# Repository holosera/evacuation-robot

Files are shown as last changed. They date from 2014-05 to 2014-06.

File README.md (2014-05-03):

evacuation-robot
================

Robot for automated evacuation of exetainer vials used in research.

Frame (acrylic sheets)

3d Printed mechanical parts 

Custom electronics (pcb and schematics)

Additional parts list

Filetypes:
.scad -> Openscad

.svg -> Inkscape

.ino -> Arduino IDE

.dxf -> Inkscape

.stl -> Meshlab

.brd -> Eagle

.sch -> Eagle

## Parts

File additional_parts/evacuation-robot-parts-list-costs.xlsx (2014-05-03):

Mechanical parts | Part # | suppliers | amount | costs $US |  | suppliers
Linear actuator Firgelli | L12-30-100-6-R | a,f | 1 | 100 |  | a | robotshop.com / robotshop.ca
Nema 17 stepper low voltage | 2.8 V 1.68A 4.4 kg-cm RepRap Stepper Motor | a,b | 1 | 30 |  | b | pololu.com
timing belt 140XL | 140XL 3/16 wide (can cut wider one) | d,e | 1 | 10 |  | c | mouser.com
hardened precsion ground shaft 8x50mm | 6112K44 | d | 2 | 10 |  | d | mcmastercarr
linear ball bearing LM8UU | LM8UU | e | 2 | 10 |  | e | ebay
Solenoid valves | U8256B045V 24volt DC (12v also works) | h | 3 | 150 |  | f | firgelli.com
Brass tee 1/8 NPT Female × Male × Female Tees | 50785K325 | d | 2 | 10 |  | g | http://www.posifamicrosystems.com/
Brass tee 1/8 NPT Female × Female × Male Tees | 50785K225 | d | 1 | 5 |  | h | valveshop.com
Medium Pressure Brass Hex Nipple 1/8 NPT | 5485K21 | d | 3 | 5
Straight Adapter for 1/4" Tube OD x 1/8 NPT Male | 5272K299 | d | 3 | 15 |  | u | none, build yourself
Straight Connector for 1/4" Tube OD | 5272K221 | d | 1 | 5
1/4 od x 1/8 id ptfe/pva tubing (1ft) |  |  | 1 | 5
1/4 od stainless steel tubing (1ft) |  |  | 1 | 5
Easy-to-Form 260 Brass | 7782T111 | d | 1 | 6
Luer lock to tube adapter | 51465K115 | d | 1 | 7
688zz ball bearing | 688zz | d | 2 | 10
Frame parts | Part # | suppliers | amount | costs $US
1/4 Acrylic sheet preferably cast | 8560K435 | d | 1 | 100
3d printed parts | minumum of 6 but up to 12 printed parts | u | x | 250 | (5 hours print time on reprap)
fasteners | #6 woodscrews, some M3 bolts | d |  | 10
Electronics | Part # | suppliers | amount | costs $US
Arduino Uno or compatible | Arduino Uno R3 | a,b,c,e | 1 | 25
Stepper motor driver DRV8825 | DRV8825 | a,b,f | 1 | 15
I2C LCD module 16x2 or 4x20 | RB-Dfr-69 or RB-Dfr-146 | a,b,c, | 1 | 25
vacuum sensor PVC1003 | PVC1003 | g | 0 | 0
EPCOS 5K thermistor for vacuum | 871-B57540G502F | c | 2 | 10 | 1 spare
PCB 1 (arduino shield) |  | u | 1 | 40
PCB 2 (vacuum sensor controller) |  | u | 1 | 30
PCB 3 (endstop) |  | u | 1 | 15
PCB 4 (rotary encoder) |  | u | 1 | 20
hookup wire, crimp connectors |  | b,c |  | 10
Power supply 12V DC 3A UL/CSA |  | a,b,c | 1 | 15
 |  | estimated | TOTAL | 948 | US dollar

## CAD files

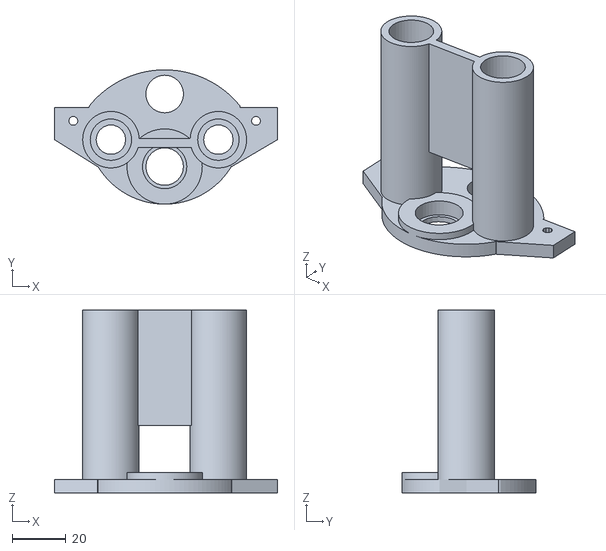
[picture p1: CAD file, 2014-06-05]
3d-printed-parts/Front-plate.stl
83.0 x 50.0 x 68.0

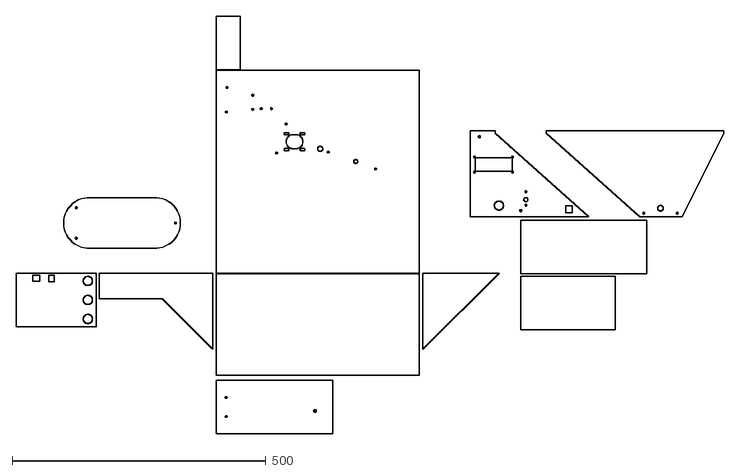
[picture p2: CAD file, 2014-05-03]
frame-sheets/acrylic_6mm_sheets.dxf
1393.8 x 822.0

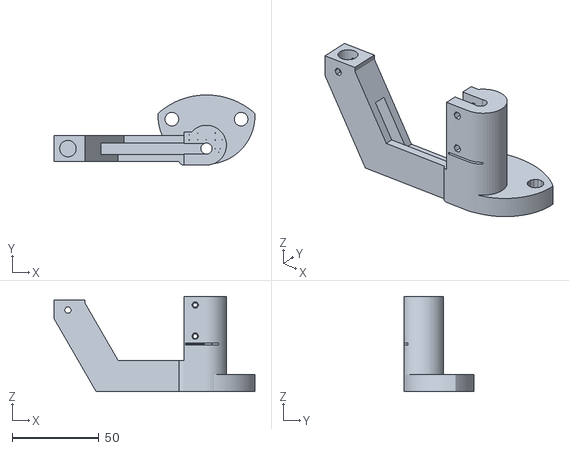
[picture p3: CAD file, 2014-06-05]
3d-printed-parts/Sled.stl
116.0 x 40.5 x 55.0

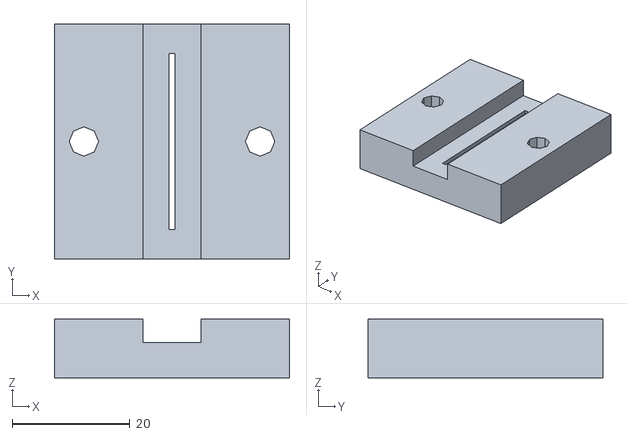
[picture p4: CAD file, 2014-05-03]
3d-printed-parts/belt-splitter_3-8_to_5mm.stl
40.0 x 40.0 x 10.0

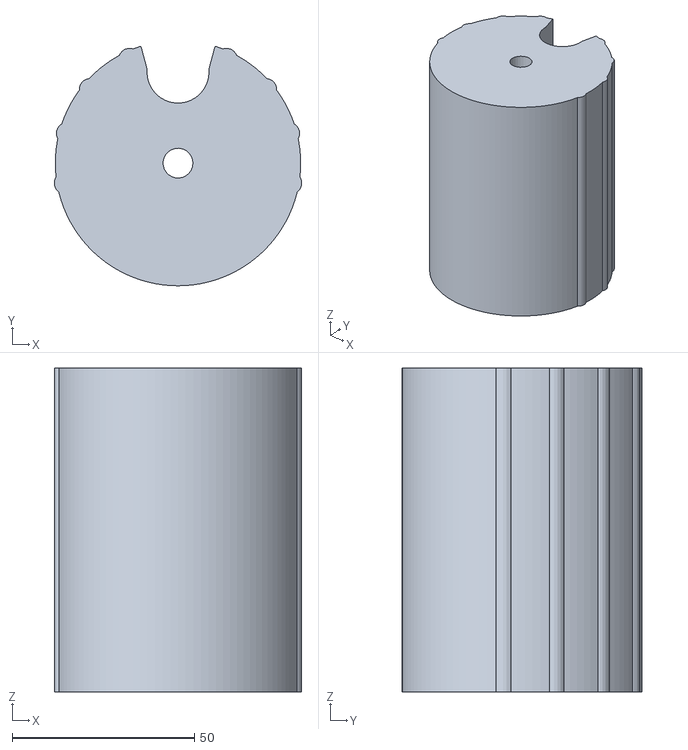
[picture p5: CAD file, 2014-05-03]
3d-printed-parts/Rotor.stl
68.0 x 65.8 x 89.0

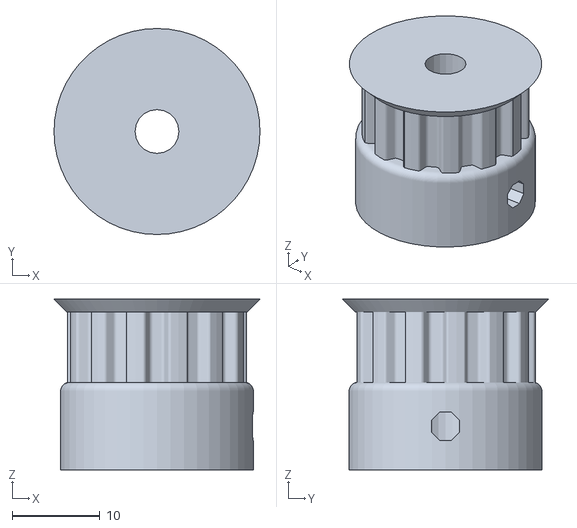
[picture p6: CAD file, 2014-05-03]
3d-printed-parts/Pulley_13T-XL.stl
23.5 x 23.5 x 19.5

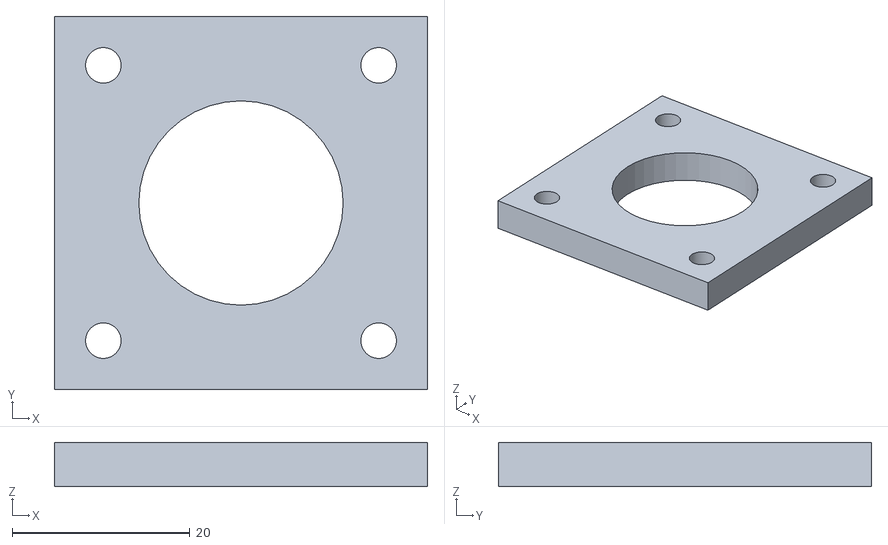
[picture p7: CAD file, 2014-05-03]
3d-printed-parts/Stepper_spacer.stl
42.0 x 42.0 x 5.00

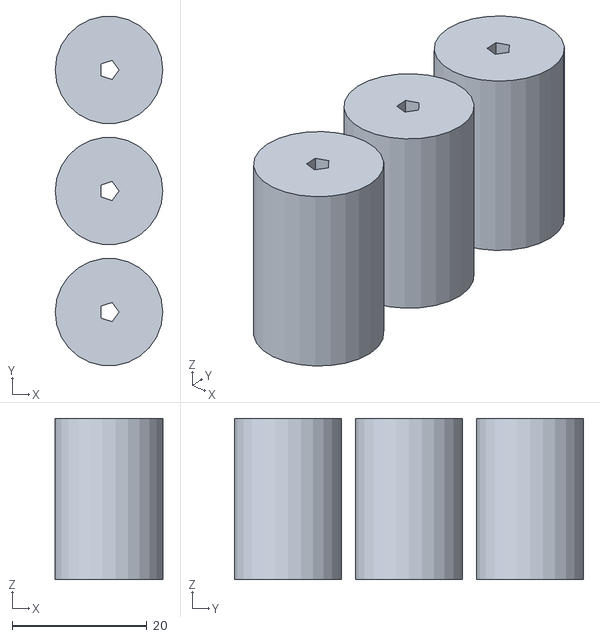
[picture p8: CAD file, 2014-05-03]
3d-printed-parts/Belt-protector-spacers.stl
16.0 x 51.9 x 24.0

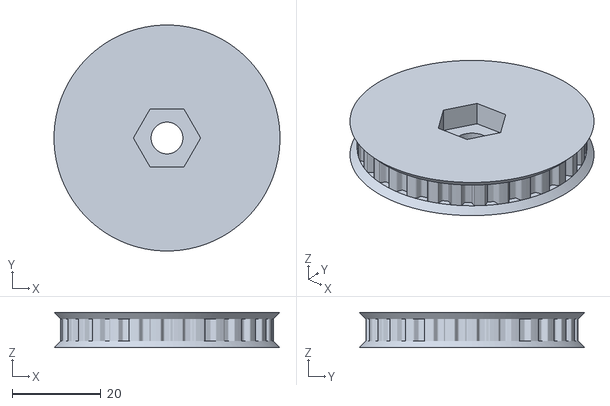
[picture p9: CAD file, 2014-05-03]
3d-printed-parts/Pulley_30T-XL.stl
51.0 x 51.0 x 8.00

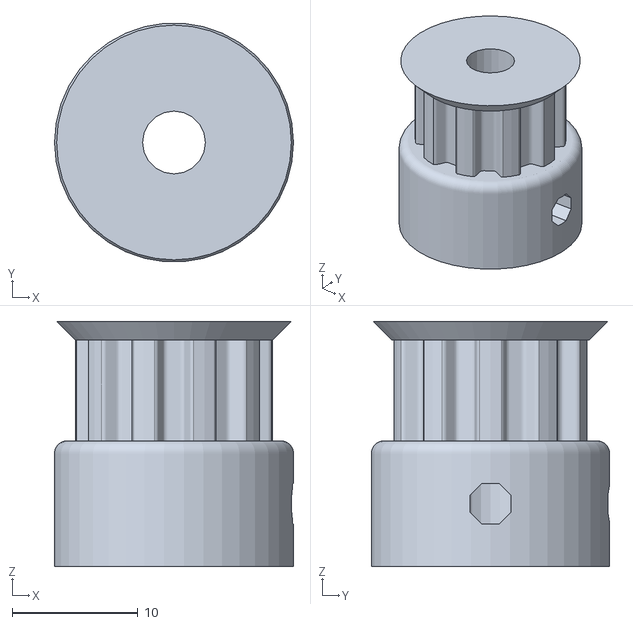
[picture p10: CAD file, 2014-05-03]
3d-printed-parts/Pulley_10T-XL.stl
19.0 x 18.9 x 19.5

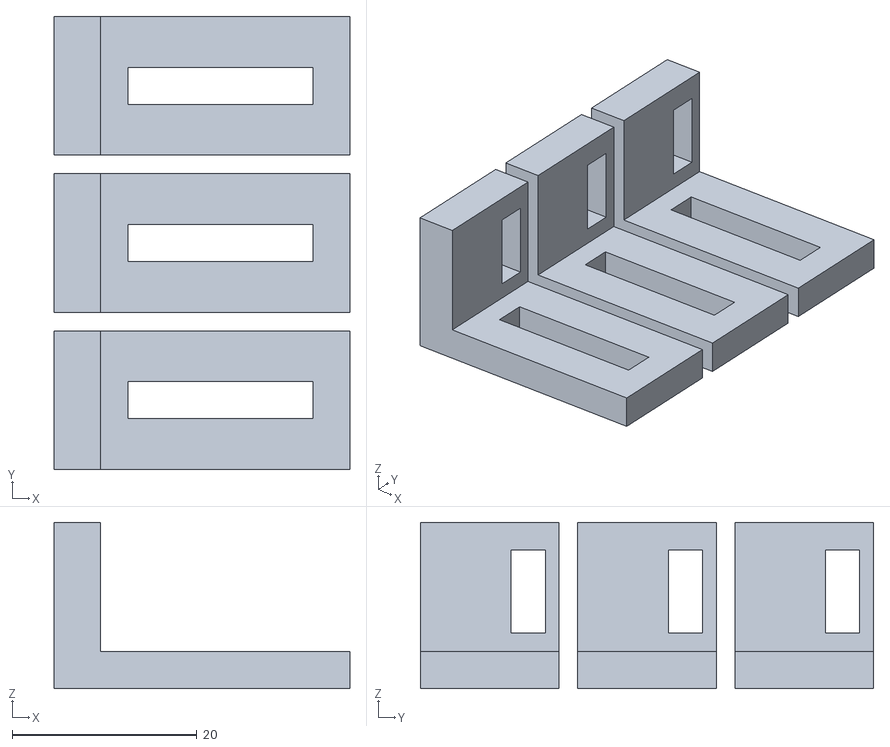
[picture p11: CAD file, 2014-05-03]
3d-printed-parts/Opto-endstop-pcb_mount.stl
32.0 x 49.0 x 18.0

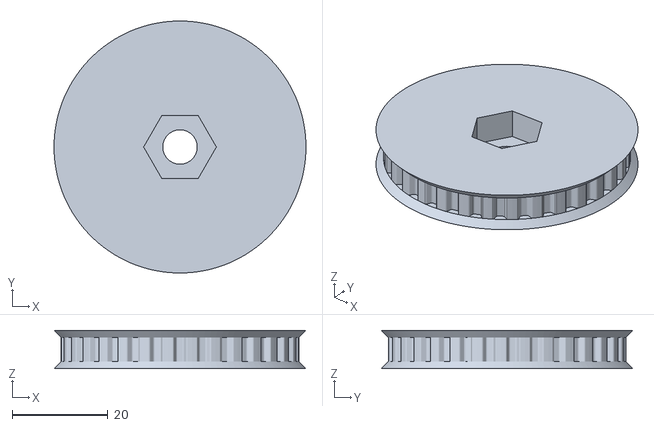
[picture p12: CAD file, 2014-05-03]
3d-printed-parts/Pulley_31T-XL.stl
52.6 x 52.6 x 8.00

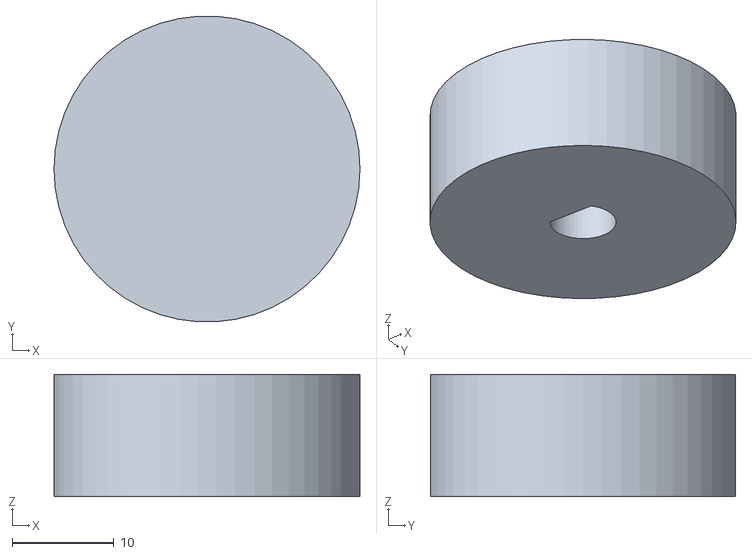
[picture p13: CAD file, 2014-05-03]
3d-printed-parts/Rotary-encoder-knob.stl
30.0 x 29.9 x 12.0

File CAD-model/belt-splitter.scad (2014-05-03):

difference(){
	translate([-20,0,0])
	cube([40,40,10]);
	translate([-4.9,-1,6])
	cube([9.8,50,50]);
	translate([-0.5,5,-1])
	cube([1,30,50]);


	translate([-15,20,-1])
	cylinder(r=2.5,h=100);
	translate([15,20,-1])
	cylinder(r=2.5,h=100);
}

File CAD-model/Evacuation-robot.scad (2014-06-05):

display=0;

sheet_thickness=6.25;
backplate_width=400;
backplate_height=400;
bottomplate_depth=200;

sideplate_height=150;
sideplate_depth=150;

slide_width=105;

//---------------------------------------------------------------------------
//_____________________ACRYLIC SHEETS__________________________________________

module bottomplate (){
	difference(){
		union(){
			translate([0,-bottomplate_depth,0])
			cube([backplate_width,bottomplate_depth,sheet_thickness]);
		}
	}
}

module backplate (){
	difference(){
		union(){
			translate([0,0,0])
			cube([backplate_width,sheet_thickness,backplate_height]);
		}
		translate([275,20,220])
		rotate([90,0,0])
		cylinder(r=4,h=100);		
	}
}

module beltplate (){
	union(){
		difference(){
			union(){
				translate([50,50,0])
				cylinder(r=50,h=sheet_thickness);	
				translate([180,50,0])
				cylinder(r=50,h=sheet_thickness);	
			}	
		translate([50,0,-1])
		cube([130,100,sheet_thickness+2]);
		}
		translate([50,0,0])
		cube([130,100,sheet_thickness]);	
	}	
}

module beltplate_holes (){
	translate([25,80,-50])
	cylinder(r=1.7,h=100);
	translate([25,20,-50])
	cylinder(r=1.7,h=100);

	translate([230-10,50,-50])
	cylinder(r=1.7,h=100);
}


module sideplateleft(){
	union(){
		translate([sheet_thickness,0,sheet_thickness])
		rotate([0,-90,0])
		linear_extrude(height=sheet_thickness)
		polygon(points=[[0,0],[0,-sideplate_depth],[sideplate_height,0]], paths=[[0,1,2]]);
		
		translate([0,-50,sheet_thickness])
		cube([sheet_thickness,50,230-sheet_thickness]);
	}
}

module sideplateright(){

	translate([backplate_width,0,sheet_thickness])
	rotate([0,-90,0])
	linear_extrude(height=sheet_thickness)

	polygon(points=[[0,0],[0,-sideplate_depth],[sideplate_height,0]], paths=[[0,1,2]]);

}

module leftslide(){
	cube([248,slide_width,sheet_thickness]);
}

module rightslide(){
	cube([186,slide_width,sheet_thickness]);
}

module slidefront(){
	difference(){
		linear_extrude(height=	sheet_thickness)
		polygon(points=[[50,0],[50,5],[234,170],[318,170],[backplate_width,5],[backplate_width,0]] , paths=[[0,1,2,3,4,5]]);	
	
	}
}

module elecfront(){
	difference(){
		translate([0,-sheet_thickness-slide_width,backplate_height])
		rotate([-90,0,0])
		linear_extrude(height=
	sheet_thickness)
		polygon(points=[[0,0],[0,170],[234,170],[50,5],[50,0]] , paths=[[0,1,2,3,4,5]]);	
	
	}
}

module elecleft (){
	difference(){
		translate([0,-slide_width,230+sheet_thickness])
		cube([sheet_thickness,slide_width,	backplate_height-230-sheet_thickness*2]);
	}
}

module electop (){
	difference(){
		translate([0,-slide_width,backplate_height-sheet_thickness])
		cube([48,slide_width,sheet_thickness]);
	}
}

module elecbottom (){
	difference(){
		translate([0,-slide_width,230])
		cube([234-4,slide_width,sheet_thickness]);
	}
}

module elecfront_connectors (){
	difference(){
		cube([24,sheet_thickness,12]);
		translate([12,-1,6])
		rotate([-90,0,0])
		cylinder(r=1.7,h=100);
	}


}

//-------------------------------------------------------------------------
//___________________________3D PRINTED PARTS______________________________

module rotor(){
	difference(){
		union(){
			translate([0,0,0])
			cylinder(r=33.7,h=89,$fn=100);
			for ( i = [-100,-75,-50,-25,0,25,50,75,100] )
			{
			    rotate( [0, 0,  i ])
			    translate([0, 31.5, 0])
			    cylinder(r=3,h=89,$fn=20);
			}
		}	
		translate([0,25,-1])
		cylinder(r=8.6,h=110,$fn=50);
		translate([0,27,-1])
		cylinder(r=8.7,h=110,$fn=50);

		translate([-8,24,-1]) 
		rotate([0,0,15])
		cube([5,40,110]);

		translate([8,24,-1])
		rotate([0,0,-15])
		translate([-5,0,0])
		cube([5,40,110]);

		translate([0,0,-2])
		cylinder(r=4.1,h=150,$fn=25);
	}
}

module sled(){
	difference(){
		union(){
			intersection(){
				translate([0,-8,0])	
				cylinder(r=28,h=10,$fn=100);
				translate([0,-38,-1])	
				cylinder(r=42,h=15,$fn=100);	
			}		

			translate([-13,-33.5,0])	
			cylinder(r=3,h=18,$fn=50);

			translate([0,-25,0])	
			cylinder(r=11.5,h=55,$fn=50);

			translate([-13,-36.5,0])
			cube([13,19,55]);

			translate([-63.7,-34.5,0])
			cube([64,15,12]);

			translate([-63.7,-34.5,0])
			cube([64,7,18]);

			translate([-88,-34.5,42])
			cube([18,15,11]);
			translate([-63.7,-34.5,0])
			rotate([0,-30,0])
			cube([20,15,48.66]);
		}	
	translate([0,-27,-1])	
	cylinder(r=3.25,h=100,$fn=20);
	translate([20,-10,-1])	
	cylinder(r=4,h=50);
	translate([-20,-10,-1])	
	cylinder(r=4,h=50);

	translate([-50,-30.25,3])	
	cube([50,6.50,24.5]);		
	translate([-50,-30,27])	
	cube([50,6,50]);	

	translate([-12,-50.0,27])	
	cube([19,22,1]);	


	translate([-6.5,0,32])	
	rotate([90,0,0])
	cylinder(r=1.4,h=100,$fn=6);	
	translate([-6.5,0,50])	
	rotate([90,0,0])
	cylinder(r=1.4,h=100,$fn=6);	

	translate([-6.5,-25,32])	
	rotate([90,0,0])
	cylinder(r=2,h=100,$fn=6);	
	translate([-6.5,-25,50])	
	rotate([90,0,0])
	cylinder(r=2,h=100,$fn=6);	

	translate([-100,-30.3,3])
	cube([54,6.5,32]);

	translate([-80,-27,15.5+28])	
	cylinder(r=4.8,h=100,$fn=20);

	translate([-80,-40,19+28])	
	rotate([-90,0,0])
	cylinder(r=2,h=100,$fn=6);


	//reinforcement
	translate([0,-22,-1])	
	cylinder(r=0.2,h=100);

	translate([-5,-22,-1])	
	cylinder(r=0.2,h=100);
	translate([5,-22,-1])	
	cylinder(r=0.2,h=100);
	translate([9,-22,-1])	
	cylinder(r=0.2,h=100);

	translate([-10,-19,-1])	
	cylinder(r=0.2,h=100);
	translate([-10,-22,-1])	
	cylinder(r=0.2,h=100);
	translate([-5,-18,-1])	
	cylinder(r=0.2,h=100);
	translate([0,-18,-1])	
	cylinder(r=0.2,h=100);
	translate([5,-18,-1])	
	cylinder(r=0.2,h=100);

	translate([5,-27,-1])	
	cylinder(r=0.2,h=100);
	translate([8,-27,-1])	
	cylinder(r=0.2,h=100);
	translate([7,-29,-1])	
	cylinder(r=0.2,h=100);
	}
	
}

module sled_old(){
	difference(){
		union(){
			intersection(){
				translate([0,-8,0])	
				cylinder(r=28,h=10,$fn=100);
				translate([0,-38,-1])	
				cylinder(r=42,h=15,$fn=100);	
			}		

			translate([-13,-33.5,0])	
			cylinder(r=3,h=18,$fn=50);

			translate([0,-25,0])	
			cylinder(r=11.5,h=55,$fn=50);

			translate([-13,-36.5,0])
			cube([13,19,55]);

			translate([-60.7,-34.5,0])
			cube([61,15,12]);

			translate([-60.7,-34.5,0])
			cube([61,7,18]);

			translate([-85,-34.5,42])
			cube([18,15,11]);
			translate([-60.7,-34.5,0])
			rotate([0,-30,0])
			cube([20,15,48.66]);
		}	
	translate([0,-27,-1])	
	cylinder(r=3.25,h=100,$fn=20);
	translate([20,-10,-1])	
	cylinder(r=4,h=50);
	translate([-20,-10,-1])	
	cylinder(r=4,h=50);

	translate([-50,-30.25,3])	
	cube([50,6.50,24.5]);		
	translate([-50,-30,27])	
	cube([50,6,50]);	

	translate([-12,-50.0,27])	
	cube([19,22,1]);	


	translate([-6.5,0,32])	
	rotate([90,0,0])
	cylinder(r=1.4,h=100,$fn=6);	
	translate([-6.5,0,50])	
	rotate([90,0,0])
	cylinder(r=1.4,h=100,$fn=6);	

	translate([-6.5,-25,32])	
	rotate([90,0,0])
	cylinder(r=2,h=100,$fn=6);	
	translate([-6.5,-25,50])	
	rotate([90,0,0])
	cylinder(r=2,h=100,$fn=6);	

	translate([-100,-30.3,3])
	cube([54,6.5,32]);

	translate([-77,-27,15.5+28])	
	cylinder(r=4.8,h=100,$fn=20);

	translate([-77,-40,19+28])	
	rotate([-90,0,0])
	cylinder(r=2,h=100,$fn=6);


	//reinforcement
	translate([0,-22,-1])	
	cylinder(r=0.2,h=100);

	translate([-5,-22,-1])	
	cylinder(r=0.2,h=100);
	translate([5,-22,-1])	
	cylinder(r=0.2,h=100);
	translate([9,-22,-1])	
	cylinder(r=0.2,h=100);

	translate([-10,-19,-1])	
	cylinder(r=0.2,h=100);
	translate([-10,-22,-1])	
	cylinder(r=0.2,h=100);
	translate([-5,-18,-1])	
	cylinder(r=0.2,h=100);
	translate([0,-18,-1])	
	cylinder(r=0.2,h=100);
	translate([5,-18,-1])	
	cylinder(r=0.2,h=100);

	translate([5,-27,-1])	
	cylinder(r=0.2,h=100);
	translate([8,-27,-1])	
	cylinder(r=0.2,h=100);
	translate([7,-29,-1])	
	cylinder(r=0.2,h=100);
	}
	
}


module frontplate(){
	difference(){
		union(){
			translate([0,0,0])
			linear_extrude(height = 5, center = false, convexity = 10, twist = 0)
			polygon(points=[[25,0],[42,10],[42,22],[-41,22],[-41,10],[-25,0]]);
			intersection() {
				cylinder(r=36,h=5,$fn=100);
				translate([0,15,-1])
				cylinder(r=29,h=7,$fn=100);	
			}			
			translate([-20,10,0])
			cylinder(r=10.5,h=68,$fn=100);	
			translate([20,10,0])
			cylinder(r=10.5,h=68,$fn=100);	

			translate([0,0,0])
			cylinder(r=14,h=7.5,$fn=100);	
			
			translate([-17.5,7,25])
			cube([35,3.5,43]);
			
		}	
	translate([0,0,-1])
	cylinder(r=7,h=100);	

	translate([20,10,-1])
	cylinder(r=5.5,h=100);	

	translate([-20,10,-1])
	cylinder(r=5.5,h=100);	

	translate([0,27,-1])
	cylinder(r=7,h=7,$fn=40);

	translate([-20,10,68-47])
	cylinder(r=7.7,h=51,$fn=40);	 
	translate([20,10,68-47])
	cylinder(r=7.7,h=51,$fn=40);	

	translate([0,0,2])
	cylinder(r=8.25,h=6,$fn=40);	
	translate([-34,17,-20])
	cylinder(r=1.7,h=38,$fn=10);	 
	translate([34,17,-20])
	cylinder(r=1.7,h=38,$fn=10);
	}

}

module frontplate_holes(){	

	translate([0,27,-50])
	cylinder(r=5.5,h=100);		

	translate([-34,17,-50])
	cylinder(r=1.7,h=108,$fn=10);	 
	translate([34,17,-20])
	cylinder(r=1.7,h=38,$fn=10);

}

module belt_protector_spacer(){
	difference(){
		cylinder(r=8,h=24);
		translate([0,0,-1])
		cylinder(r=1.5,h=100);
	}
}
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

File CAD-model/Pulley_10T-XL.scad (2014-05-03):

// Parametric Pulley with multiple belt profiles
// by droftarts January 2012

// Based on pulleys by:
// http://www.thingiverse.com/thing:11256 by me!
// https://github.com/prusajr/PrusaMendel by Josef Prusa
// http://www.thingiverse.com/thing:3104 by GilesBathgate
// http://www.thingiverse.com/thing:2079 by nophead

// dxf tooth data from http://oem.cadregister.com/asp/PPOW_Entry.asp?company=915217&elementID=07807803/METRIC/URETH/WV0025/F
// pulley diameter checked and modelled from data at http://www.sdp-si.com/D265/HTML/D265T016.html

/**
 * @name Pulley
 * @category Printed
 * @using 1 x m3 nut, normal or nyloc
 * @using 1 x m3x10 set screw or 1 x m3x8 grub screw
 */

516nutdiam=15.2;


// tuneable constants

teeth = 10;			// Number of teeth, standard Mendel T5 belt = 8, gives Outside Diameter of 11.88mm
profile = 3;		// 1=MXL 2=40DP 3=XL 4=H 5=T2.5 6=T5 7=T10 8=AT5 9=HTD_3mm 10=HTD_5mm 11=HTD_8mm 12=GT2_2mm 13=GT2_3mm 14=GT2_5mm

motor_shaft = 5;	// NEMA17 motor shaft exact diameter = 5
m3_dia = 0.5;		// 3mm hole diameter
m3_nut_hex = 1;		// 1 for hex, 0 for square nut
m3_nut_flats = 5.7;	// normal M3 hex nut exact width = 5.5
m3_nut_depth = 2.7;	// normal M3 hex nut exact depth = 2.4, nyloc = 4

retainer = 1;		// Belt retainer above teeth, 0 = No, 1 = Yes
retainer_ht = 1.5;	// height of retainer flange over pulley, standard = 1.5
idler = 1;			// Belt retainer below teeth, 0 = No, 1 = Yes
idler_ht = 1.5;		// height of idler flange over pulley, standard = 1.5

pulley_t_ht = 8;	// length of toothed part of pulley, standard = 12
pulley_b_ht = 10;		// pulley base height, standard = 8. Set to same as idler_ht if you want an idler but no pulley.
pulley_b_dia = 20;	// pulley base diameter, standard = 20
no_of_nuts = 1;		// number of captive nuts required, standard = 1
nut_angle = 90;		// angle between nuts, standard = 90
nut_shaft_distance = 10;	// distance between inner face of nut and shaft, can be negative.




//	********************************
//	** Scaling tooth for good fit **
//	********************************
/*	To improve fit of belt to pulley, set the following constant. Decrease or increase by 0.1mm at a time. We are modelling the *BELT* tooth here, not the tooth on the pulley. Increasing the number will *decrease* the pulley tooth size. Increasing the tooth width will also scale proportionately the tooth depth, to maintain the shape of the tooth, and increase how far into the pulley the tooth is indented. Can be negative */

additional_tooth_width = 0.2; //mm

//	If you need more tooth depth than this provides, adjust the following constant. However, this will cause the shape of the tooth to change.

additional_tooth_depth = 0; //mm

// calculated constants

nut_elevation = pulley_b_ht/2;
m3_nut_points = 2*((m3_nut_flats/2)/cos(30)); // This is needed for the nut trap

// The following set the pulley diameter for a given number of teeth

MXL_pulley_dia = tooth_spacing (2.032,0.254);
40DP_pulley_dia = tooth_spacing (2.07264,0.1778);
XL_pulley_dia = tooth_spacing (5.08,0.254);
H_pulley_dia = tooth_spacing (9.525,0.381);
T2_5_pulley_dia = tooth_spaceing_curvefit (0.7467,0.796,1.026);
T5_pulley_dia = tooth_spaceing_curvefit (0.6523,1.591,1.064);
T10_pulley_dia = tooth_spacing (10,0.93);
AT5_pulley_dia = tooth_spaceing_curvefit (0.6523,1.591,1.064);
HTD_3mm_pulley_dia = tooth_spacing (3,0.381);
HTD_5mm_pulley_dia = tooth_spacing (5,0.5715);
HTD_8mm_pulley_dia = tooth_spacing (8,0.6858);
GT2_2mm_pulley_dia = tooth_spacing (2,0.254);
GT2_3mm_pulley_dia = tooth_spacing (3,0.381);
GT2_5mm_pulley_dia = tooth_spacing (5,0.5715);

// The following calls the pulley creation part, and passes the pulley diameter and tooth width to that module

if ( profile == 1 ) { pulley ( "MXL" , MXL_pulley_dia , 0.508 , 1.321 ); }
if ( profile == 2 ) { pulley ( "40 D.P." , 40DP_pulley_dia , 0.457 , 1.226 ); }
if ( profile == 3 ) { 
//	difference(){
		pulley ( "XL" , XL_pulley_dia , 1.27, 3.051 ); 
//		
//		translate([0,0,7.1])
//		cylinder(r=516nutdiam/2, h=6, $fn=6);
//	}
}
if ( profile == 4 ) { pulley ( "H" , H_pulley_dia ,1.905 , 5.359 ); }
if ( profile == 5 ) { pulley ( "T2.5" , T2_5_pulley_dia , 0.7 , 1.678 ); }
if ( profile == 6 ) { pulley ( "T5" , T5_pulley_dia , 1.19 , 3.264 ); }
if ( profile == 7 ) { pulley ( "T10" , T10_pulley_dia , 2.5 , 6.13 ); }
if ( profile == 8 ) { pulley ( "AT5" , AT5_pulley_dia , 1.19 , 4.268 ); }
if ( profile == 9 ) { pulley ( "HTD 3mm" , HTD_3mm_pulley_dia , 1.289 , 2.27 ); }
if ( profile == 10 ) { pulley ( "HTD 5mm" , HTD_5mm_pulley_dia , 2.199 , 3.781 ); }
if ( profile == 11 ) { pulley ( "HTD 8mm" , HTD_8mm_pulley_dia , 3.607 , 6.603 ); }
if ( profile == 12 ) { pulley ( "GT2 2mm" , GT2_2mm_pulley_dia , 0.764 , 1.494 ); }
if ( profile == 13 ) { pulley ( "GT2 3mm" , GT2_3mm_pulley_dia , 1.169 , 2.31 ); }
if ( profile == 14 ) { pulley ( "GT2 5mm" , GT2_5mm_pulley_dia , 1.969 , 3.952 ); }

// Functions

function tooth_spaceing_curvefit (b,c,d)
	= ((c * pow(teeth,d)) / (b + pow(teeth,d))) * teeth ;

function tooth_spacing(tooth_pitch,pitch_line_offset)
	= (2*((teeth*tooth_pitch)/(3.14159265*2)-pitch_line_offset)) ;

// Main Module

module pulley( belt_type , pulley_OD , tooth_depth , tooth_width )
	{
	echo (str("Belt type = ",belt_type,"; Number of teeth = ",teeth,"; Pulley Outside Diameter = ",pulley_OD,"mm "));
	tooth_distance_from_centre = sqrt( pow(pulley_OD/2,2) - pow((tooth_width+additional_tooth_width)/2,2));
	tooth_width_scale = (tooth_width + additional_tooth_width ) / tooth_width;
	tooth_depth_scale = ((tooth_depth + additional_tooth_depth ) / tooth_depth) ;


//	************************************************************************
//	*** uncomment the following line if pulley is wider than puller base ***
//	************************************************************************

//	translate ([0,0, pulley_b_ht + pulley_t_ht + retainer_ht ]) rotate ([0,180,0])

	difference()
	 {	 
		union()
		{
			//base
	
			if ( pulley_b_ht < 2 ) { echo ("CAN'T DRAW PULLEY BASE, HEIGHT LESS THAN 2!!!"); } else {
				rotate_extrude($fn=pulley_b_dia*2)
				{
						square([pulley_b_dia/2-1,pulley_b_ht]);
						square([pulley_b_dia/2,pulley_b_ht-1]);
						translate([pulley_b_dia/2-1,pulley_b_ht-1]) circle(1);
				}
			}
	
		difference()
			{
			//shaft - diameter is outside diameter of pulley
			
			translate([0,0,pulley_b_ht]) 
			rotate ([0,0,360/(teeth*4)]) 
			cylinder(r=pulley_OD/2,h=pulley_t_ht, $fn=teeth*4);
	
			//teeth - cut out of shaft
		
			for(i=[1:teeth]) 
			rotate([0,0,i*(360/teeth)])
			translate([0,-tooth_distance_from_centre,pulley_b_ht -1]) 
			scale ([ tooth_width_scale , tooth_depth_scale , 1 ]) 
			{
			if ( profile == 1 ) { MXL();}
			if ( profile == 2 ) { 40DP();}
			if ( profile == 3 ) { XL();}
			if ( profile == 4 ) { H();}
			if ( profile == 5 ) { T2_5();}
			if ( profile == 6 ) { T5();}
			if ( profile == 7 ) { T10();}
			if ( profile == 8 ) { AT5();}
			if ( profile == 9 ) { HTD_3mm();}
			if ( profile == 10 ) { HTD_5mm();}
			if ( profile == 11 ) { HTD_8mm();}
			if ( profile == 12 ) { GT2_2mm();}
			if ( profile == 13 ) { GT2_3mm();}
			if ( profile == 14 ) { GT2_5mm();}
			}

			}
			
		//belt retainer / idler
		if ( retainer > 0 ) {translate ([0,0, pulley_b_ht + pulley_t_ht ]) 
		rotate_extrude($fn=teeth*4)  
		polygon([[0,0],[pulley_OD/2,0],[pulley_OD/2 + retainer_ht , retainer_ht],[0 , retainer_ht],[0,0]]);}
		
		if ( idler > 0 ) {translate ([0,0, pulley_b_ht - idler_ht ]) 
		rotate_extrude($fn=teeth*4)  
		polygon([[0,0],[pulley_OD/2 + idler_ht,0],[pulley_OD/2 , idler_ht],[0 , idler_ht],[0,0]]);}
	
		}
	   
		//hole for motor shaft
		translate([0,0,-1])cylinder(r=motor_shaft/2,h=pulley_b_ht + pulley_t_ht + retainer_ht + 2,$fn=motor_shaft*4);
				
		//captive nut and grub screw holes
	
		if ( pulley_b_ht < m3_nut_flats ) { echo ("CAN'T DRAW CAPTIVE NUTS, HEIGHT LESS THAN NUT DIAMETER!!!"); } else {
		if ( (pulley_b_dia - motor_shaft)/2 < m3_nut_depth + 3 ) { echo ("CAN'T DRAW CAPTIVE NUTS, DIAMETER TOO SMALL FOR NUT DEPTH!!!"); } else {
	
			for(j=[1:no_of_nuts]) rotate([0,0,j*nut_angle])
			translate([0,0,nut_elevation])rotate([90,0,0])
	
			union()
			{
				//entrance
				translate([0,-pulley_b_ht/4-0.5,motor_shaft/2+m3_nut_depth/2+nut_shaft_distance]) cube([m3_nut_flats,pulley_b_ht/2+1,m3_nut_depth],center=true);
	
				//nut
				if ( m3_nut_hex > 0 )
					{
						// hex nut
						translate([0,0.25,motor_shaft/2+m3_nut_depth/2+nut_shaft_distance]) rotate([0,0,30]) cylinder(r=m3_nut_points/2,h=m3_nut_depth,center=true,$fn=6);
					} else {
						// square nut
						translate([0,0.25,motor_shaft/2+m3_nut_depth/2+nut_shaft_distance]) cube([m3_nut_flats,m3_nut_flats,m3_nut_depth],center=true);
					}
	
				//grub screw hole
				rotate([0,0,22.5])cylinder(r=m3_dia/2,h=pulley_b_dia/2+1,$fn=8);
			}
		}}
	 }
	   
	}


// Tooth profile modules
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

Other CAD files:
CAD-model/Pulley_13T-XL.scad
CAD-model/Pulley_30T-XL.scad
CAD-model/Pulley_31T-XL.scad
CAD-model/rotary_encoder-knob.scad
CAD-model/stepper_spacer.scad

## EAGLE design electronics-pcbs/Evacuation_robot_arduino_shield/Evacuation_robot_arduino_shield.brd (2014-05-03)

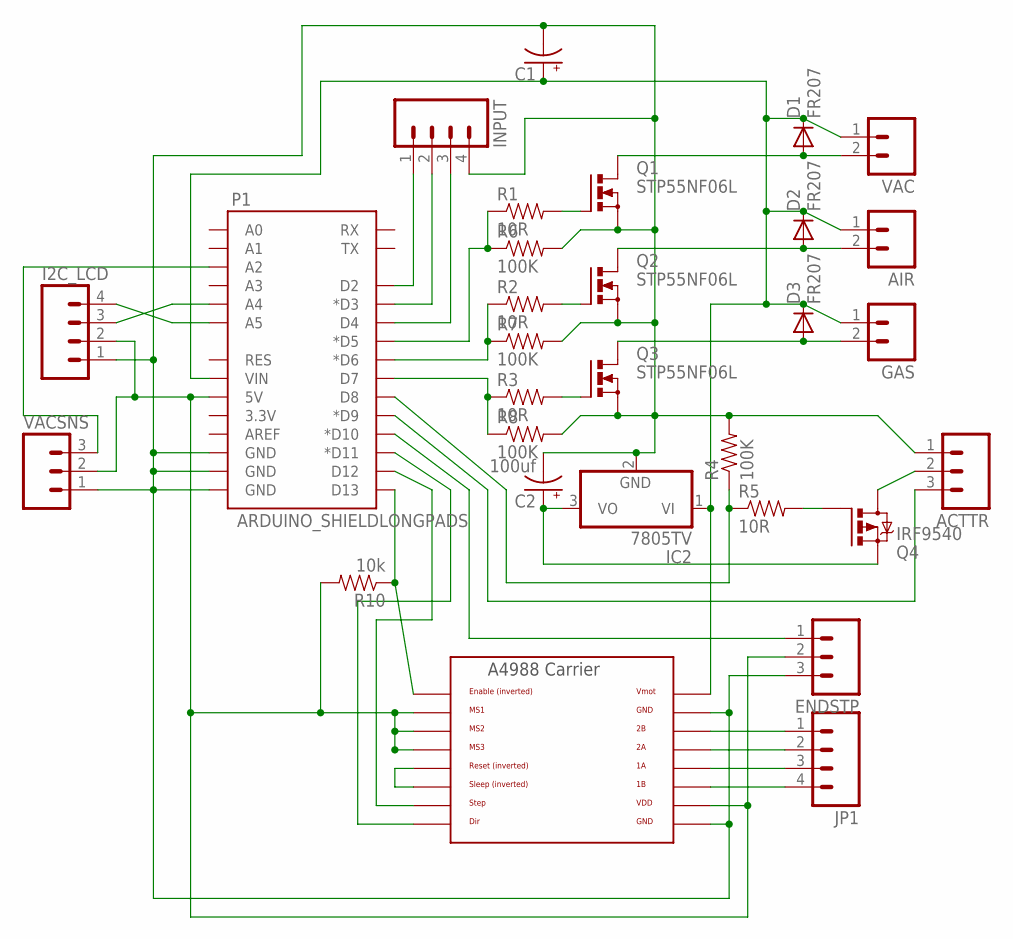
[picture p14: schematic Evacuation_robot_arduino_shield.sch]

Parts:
ACTTR: M03LONGPADS; 1X03_LONGPADS
AIR: M02PTH3; 1X02_LONGPADS
C1: CAP_POLPTH4; CPOL-RADIAL-1000UF-25V
C2: 100uf; CPOL-RADIAL-100UF-25V
D1, D2, D3: FR207; DIODE-1N4148
ENDSTP: M03LONGPADS; 1X03_LONGPADS
GAS: M02PTH3; 1X02_LONGPADS
I2C_LCD: M04LONGPADS; 1X04_LONGPADS
IC2: 7805TV; TO220V
INPUT: M04LONGPADS; 1X04_LONGPADS
JP1: M04LONGPADS; 1X04_LONGPADS
P1: ARDUINO_SHIELDLONGPADS; DUEMILANOVE_SHIELD_LONGPADS
Q1, Q2, Q3: STP55NF06L; TO220BV
Q4: IRF9540; TO220BV
R1, R2, R3, R5: 10R; AXIAL-0.3
R4, R6, R7, R8: 100K; AXIAL-0.3
R10: 10k; AXIAL-0.3
U$1: A4988BREAKOUT
VAC: M02PTH3; 1X02_LONGPADS
VACSNS: M03LONGPADS; 1X03_LONGPADS

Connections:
unnamed: INPUT.3, P1.D4
unnamed: INPUT.2, P1.D3 (*D3)
unnamed: P1.D6 (*D6), R2.P$1 (1), R7.P$1 (1)
unnamed: P1.D7, R3.P$1 (1), R8.P$1 (1)
unnamed: P1.D5 (*D5), R1.P$1 (1), R6.P$1 (1)
unnamed: ENDSTP.1, P1.D10 (*D10)
unnamed: Q1.G, R1.P$2 (2)
unnamed: JP1.1, U$1.2B
unnamed: INPUT.1, P1.D2
unnamed: Q3.G, R3.P$2 (2)
unnamed: Q2.G, R2.P$2 (2)
unnamed: D1.A, Q1.D, VAC.2
unnamed: AIR.2, D2.A, Q2.D
unnamed: D3.A, GAS.2, Q3.D
unnamed: I2C_LCD.3, P1.A4
unnamed: JP1.2, U$1.2A
unnamed: I2C_LCD.4, P1.A5
unnamed: AIR.1, C1.1 (+), D1.C, D2.C, D3.C, GAS.1, IC2.1 (VI), P1.VIN, U$1.VMOT, VAC.1
unnamed: JP1.3, U$1.1A
unnamed: JP1.4, U$1.1B
unnamed: U$1.RST, U$1.SLP (SLEEP)
unnamed: ACTTR.3, P1.D9 (*D9)
unnamed: Q4.G, R5.P$2 (2)
unnamed: P1.D13, R10.P$1 (1), U$1.EN
unnamed: P1.D11 (*D11), U$1.DIR
unnamed: P1.D8, R4.P$1 (1), R5.P$1 (1)
unnamed: P1.A2, VACSNS.3
unnamed: C2.1 (+), IC2.3 (VO), Q4.S
unnamed: P1.D12, U$1.STEP
unnamed: ACTTR.2, Q4.D
unnamed: ENDSTP.2, I2C_LCD.2, P1.5V, R10.P$2 (2), U$1.MS1, U$1.MS2, U$1.MS3, U$1.VDD, VACSNS.2
unnamed: ACTTR.1, C1.2 (-), C2.2 (-), ENDSTP.3, I2C_LCD.1, IC2.2 (GND), INPUT.4, P1.GND@0 (GND), P1.GND@1 (GND), P1.GND@2 (GND), Q1.S, Q2.S, Q3.S, R4.P$2 (2), R6.P$2 (2), R7.P$2 (2), R8.P$2 (2), U$1.GND, U$1.GND@0 (GND), VACSNS.1

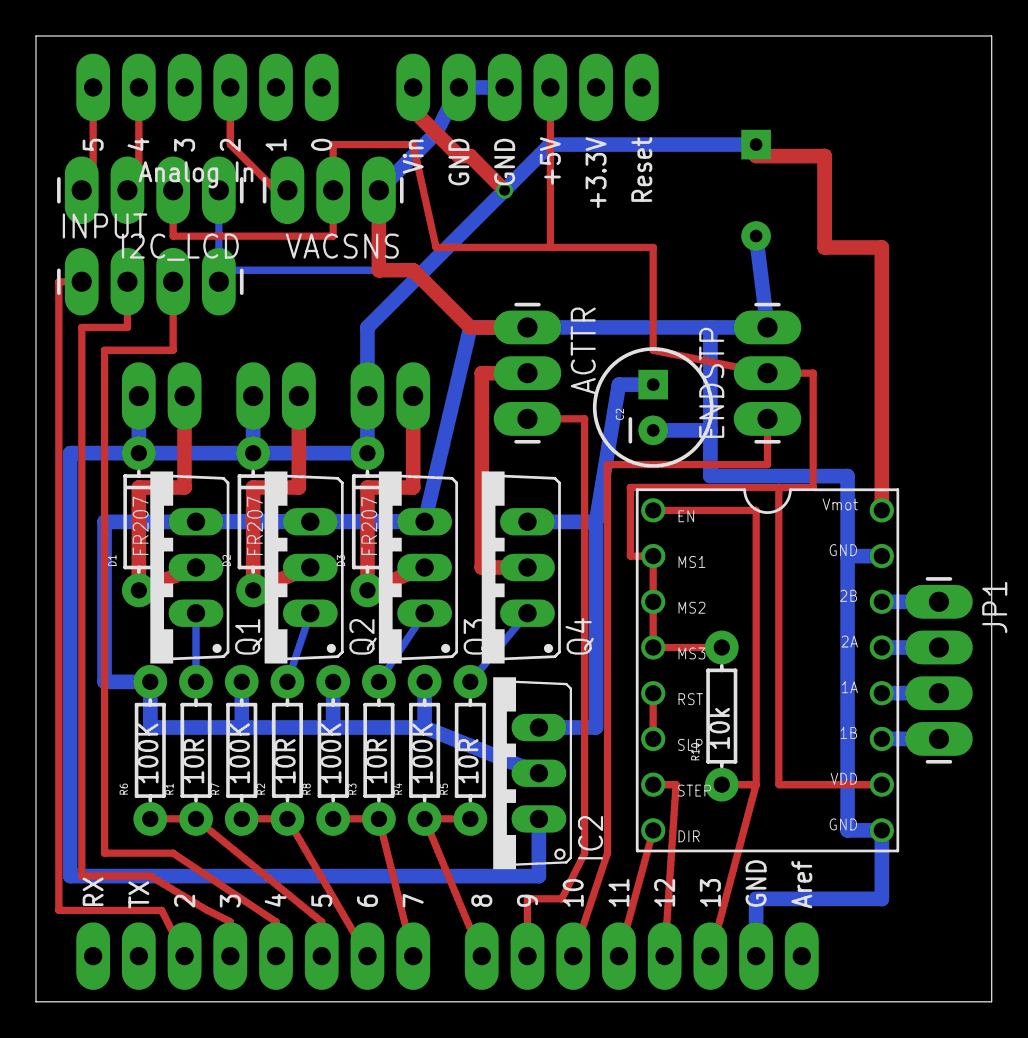
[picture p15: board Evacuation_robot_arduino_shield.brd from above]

Board: 2 copper layers, 53.1 x 53.7 mm, 30 parts (1 on the bottom side), 32 nets.

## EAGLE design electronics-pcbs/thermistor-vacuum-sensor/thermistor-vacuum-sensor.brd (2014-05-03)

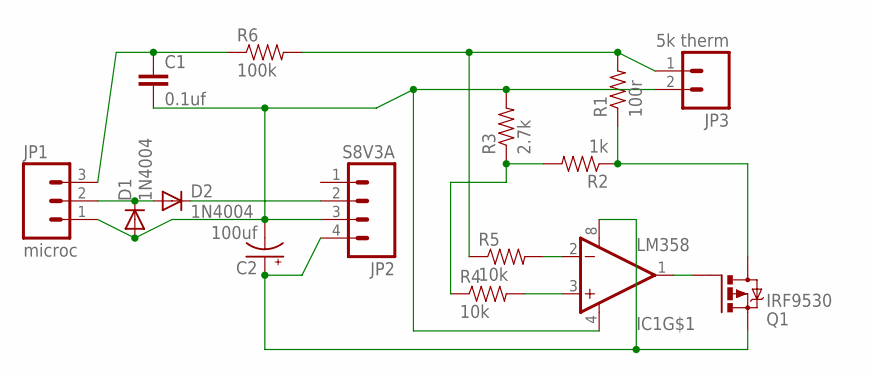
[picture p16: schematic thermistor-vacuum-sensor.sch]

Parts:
C1: 0.1uf; CAP-PTH-SMALL
C2: 100uf; CPOL-RADIAL-100UF-25V
D1, D2: 1N4004; DO41-10
IC1: LM358; DIP08
JP1: microc; 1X03_LONGPADS
JP2: S8V3A; 1X04_LONGPADS
JP3: 5k therm; 1X02_LOCK_LONGPADS
Q1: IRF9530; TO220BV
R1: 100r; AXIAL-0.3
R2: 1k; AXIAL-0.3
R3: 2.7k; AXIAL-0.3
R4, R5: 10k; AXIAL-0.3
R6: 100k; AXIAL-0.3

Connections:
unnamed: D1.C, D2.A, JP1.2
unnamed: D2.C, JP2.2
unnamed: C1.2, C2.2 (-), D1.A, IC1.4 (V-), JP1.1, JP2.3, JP3.2, R3.P$2 (2)
unnamed: C2.1 (+), IC1.8 (V+), JP2.4, Q1.S
unnamed: C1.1, JP1.3, R6.P$1 (1)
unnamed: IC1.2 (-IN), R5.P$2 (2)
unnamed: IC1.3 (+IN), R4.P$2 (2)
unnamed: IC1.1 (OUT), Q1.G
unnamed: JP3.1, R1.P$2 (2), R5.P$1 (1), R6.P$2 (2)
unnamed: R2.P$2 (2), R3.P$1 (1), R4.P$1 (1)
unnamed: Q1.D, R1.P$1 (1), R2.P$1 (1)

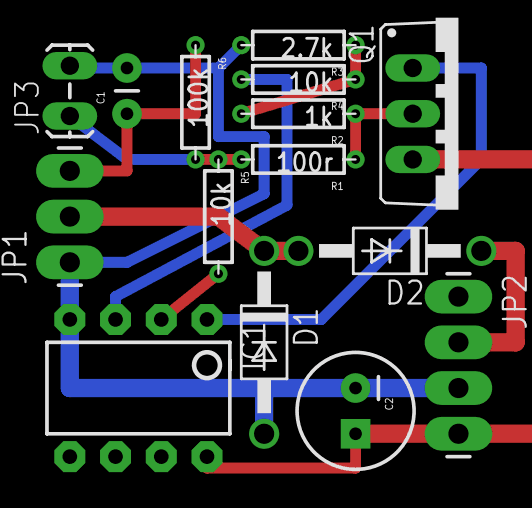
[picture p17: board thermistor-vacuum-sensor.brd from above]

Board: 2 copper layers, 15 parts (0 on the bottom side), 11 nets.

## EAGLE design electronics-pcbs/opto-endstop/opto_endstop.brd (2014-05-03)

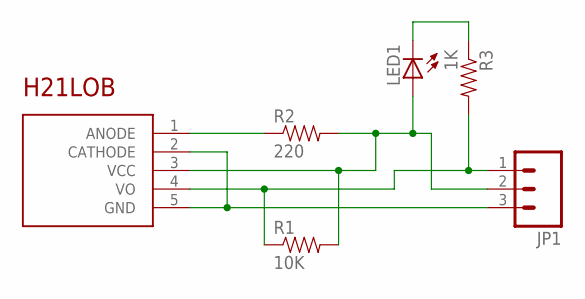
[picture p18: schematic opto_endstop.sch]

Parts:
JP1: M03LONGPADS; 1X03_LONGPADS
LED1: LED5MM
R1: 10K; AXIAL-0.3
R2: 220; AXIAL-0.3
R3: 1K; AXIAL-0.3
U$2: H21LOB; H21

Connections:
unnamed: R2.P$1 (1), U$2.1 (ANODE)
unnamed: JP1.2, LED1.A, R1.P$2 (2), R2.P$2 (2), U$2.3 (VCC)
unnamed: JP1.3, U$2.2 (CATHODE), U$2.5 (GND)
unnamed: JP1.1, R1.P$1 (1), R3.P$2 (2), U$2.4 (VO)
unnamed: LED1.K (C), R3.P$1 (1)

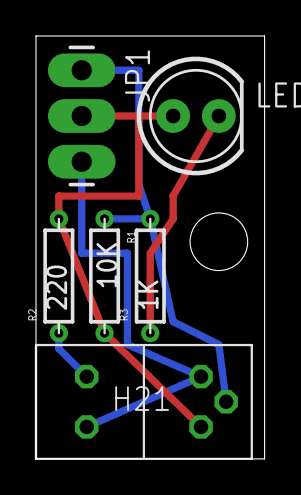
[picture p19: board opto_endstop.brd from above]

Board: 2 copper layers, 12.7 x 23.5 mm, 6 parts (0 on the bottom side), 5 nets.

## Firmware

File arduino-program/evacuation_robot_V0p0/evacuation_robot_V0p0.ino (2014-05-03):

#include <EEPROM.h> // functions to read and write eeprom
#include <Wire.h>
#include <LCDi2cNHD.h> // include the library code:
#include "config.h"
#include <Encoder.h>

//____________________declare variables_____________________________
// define the LCD address is 0x50>>1 which equals 0x28 NEWHEAVEN
LCDi2cNHD lcd = LCDi2cNHD(2,16,0x50>>1,0);



Encoder myEnc(EncoderA, EncoderB);

int amountmenuitems=11;
char menuitems[11][19] = {"evac.program      ",  //0
                     "evac.target       ",  //1
                     "max.evac.time     ",  //2
                     "rot.center        ",  //3
                     "needle.in         ",  //4
                     "needle.out        ",  //5
                     "max.bad.in.row    ", //6
                     "flush.air.time    ", //7
                     "flush.gas.time    ", //8
                     "pre.flush.air     ", //9
                     "back.start.program"};//10
                      
int defaultvalues[11]={0,   //evac.program
                      55,   //evac.target
                      180,  //max.evac.time
                      0, //rot.servo.center
                      1000, //needle.servo.in
                      2000, //needle.servo.out
                      5,    //max.bad.in.row
                      5,   //flush.air.time
                      5,   //flush.gas.time
                      0 }; // pre-flush with air

char menuOptions[3][19] = {
                     "Save setting      ",  //0
                     "Test setting      ",  //1
                     "Dont save setting "};  //2


int evacprogram;
int evactarget;
int maxevactime;  
int rotcenter;
int needlein;
int needleout;
int maxbadinrow;
int flushairtime;
int flushgastime;
int preflushair;

int rotbitleft;
int rotbitright;
int rotdropbad;
int rotdropgood;
int halfevactarget;
int rotposnow;

//vacuum gauge
float runavgvac=1023.0; // running average of pwm needed for therm
unsigned long timelastvacread=millis();
float vacstart=1023.0;
float vacpercnow=100.0;
float tempfloat;

int tempint; // reusable temporary variable

long oldPosition=0;
long newPosition=0;
int encoderPressed=0;
int encoderChanged=0;
long timeLastPosition=millis();

int counter; 
unsigned long startMillis = millis();
unsigned long curMillis;  
unsigned long startMillis2= millis();

int tubegood=0;
int curposus=0;
int badinrow=0;


//---------------------------------------------------------------------------------------------
//______________________________ MAIN PROGRAM__________________________________________________
//---------------------------------------------------------------------------------------------
void setup() {
  delay(150); // let the chip stabilize
  pinMode(thermpin, INPUT);
  pinMode(vacvpin, OUTPUT);      // sets the digital pin as output
  pinMode(gasvpin, OUTPUT);      // sets the digital pin as output
  pinMode(airvpin, OUTPUT);      // sets the digital pin as output
  pinMode(needlepowerpin, OUTPUT);    // sets the digital pin as output
  pinMode(needlecontrolpin, OUTPUT);    // sets the digital pin as output
  
  pinMode(rotenpin, OUTPUT);    // sets the digital pin as output
  pinMode(rotdirpin, OUTPUT);    // sets the digital pin as output
  pinMode(rotsteppin, OUTPUT);    // sets the digital pin as output
  pinMode(optopin, INPUT);    // sets the digital pin as input

  digitalWrite(vacvpin, LOW);     // sets the digital pin low
  digitalWrite(gasvpin, LOW);     // sets the digital pin low
  digitalWrite(airvpin, LOW);     // sets the digital pin low
  digitalWrite(needlepowerpin, LOW);   // sets the digital pin low
  digitalWrite(needlecontrolpin, LOW);   // sets the digital pin low
  
  digitalWrite(rotenpin, HIGH);      // sets the digital pin high (inverted input)
  digitalWrite(rotdirpin, LOW);      // sets the digital pin low
  digitalWrite(rotsteppin, LOW);      // sets the digital pin low
  
  pinMode(EncoderPress, INPUT);    // sets the digital pin as input
  digitalWrite(EncoderPress, HIGH);      // sets pull-up of the digital pin high
  digitalWrite(optopin, LOW);      // sets pull-up of the digital pin high

  oldPosition = myEnc.read();
  newPosition = myEnc.read();
  
  //start the LCD
  lcd.init();                     // Init the display, clears the display
  lcd.setDelay (100,1);
  delay(100);
  printwelcome();
                      
  evacprogram=readinteeprom(firsteepromaddress+2*0);
  evactarget=readinteeprom(firsteepromaddress+2*1);
  maxevactime=readinteeprom(firsteepromaddress+2*2);  
  rotcenter=readinteeprom(firsteepromaddress+2*3);
  needlein=readinteeprom(firsteepromaddress+2*4);
  needleout=readinteeprom(firsteepromaddress+2*5);
  maxbadinrow=readinteeprom(firsteepromaddress+2*6);
  flushairtime=readinteeprom(firsteepromaddress+2*7);
  flushgastime=readinteeprom(firsteepromaddress+2*8);
  
  rotbitleft= rotcenter-rotshake;
  rotbitright= rotcenter+rotshake;
  rotdropgood= rotcenter+rotdrop;
  rotdropbad= rotcenter-rotdrop;
  halfevactarget= (100-(100-evactarget)/2);
  
  allhome();
}


void loop() {
  if (preflushair>0) { // if helium or hydrogen is attached do pwmzero in air
    flushlines();
    pwmzero();  
  }
  if (evacprogram!=0) { //if temperature of vacuum sensor is ok
      stirandgrab(); // grab tube and put needle in    
      
      if (evacprogram==1)  {
          flushair();
          if (preflushair<1){ pwmzero(); }
          evacuate(evactarget);          
      }
      else if (evacprogram==2) {
          flushair();
          if (preflushair<1){ pwmzero(); }
          evacuate(evactarget);
          flushair();
          evacuate(evactarget);
      }
      else if (evacprogram==3) {
          flushair();
          if (preflushair<1){ pwmzero(); }        
          evacuate(halfevactarget);
          flushair();
          evacuate(evactarget);
      }
      else if (evacprogram==4) {
          flushair();
          if (preflushair<1){ pwmzero(); }        
          evacuate(halfevactarget);
          flushair();
          evacuate(halfevactarget);
          flushair();
          evacuate(evactarget);
      }
      else if (evacprogram==5) {
          flushgas();
          flushair();
          if (preflushair<1){ pwmzero(); }
          evacuate(evactarget);
      }
      else if (evacprogram==6) {
          flushgas();
          flushair();
          if (preflushair<1){ pwmzero(); }
          evacuate(evactarget);
          flushgas();
          flushair();
          evacuate(evactarget);
      }    
      else if (evacprogram==7) {
          flushgas();
          flushair();
          if (preflushair<1){ pwmzero(); }
          evacuate(halfevactarget);
          flushgas();
          flushair();
          evacuate(evactarget);
      }  
      else if (evacprogram==8) {
          flushgas();
          flushair();
          if (preflushair<1){ pwmzero(); }
          evacuate(halfevactarget);
          flushgas();
          flushair();
          evacuate(halfevactarget);
          flushgas();
          flushair();
          evacuate(evactarget);
      }  
       else if (evacprogram==9) {
          flushair(); 
          if (preflushair<1){ pwmzero(); }
          evacuate(evactarget);
          flushgas();
          flushair();
      }       
       else if (evacprogram==10) {
          flushgas();
          flushair();
          if (preflushair<1){ pwmzero(); }
          evacuate(evactarget);
          flushgas();
          flushair();
      }   
      else if (evacprogram==11) {
          flushgas();
          flushair();
          if (preflushair<1){ pwmzero(); }
          evacuate(halfevactarget);
          flushgas();
          flushair();
          evacuate(evactarget);
          flushgas();
          flushair();
      } 
      
      else if (evacprogram==12) {
          flushgas();
          flushair();
          if (preflushair<1){ pwmzero(); }
          evacuate(evactarget);
          flushgas();
      } 
      else if (evacprogram==13) {
          flushgas();
          flushair();
          if (preflushair<1){ pwmzero(); }
          evacuate(halfevactarget);
          flushgas();
          flushair();
          evacuate(evactarget);
          flushgas();
      }    
      
      // ADD MORE PROGRAMS HERE

      else {
         lcd.clear(); 
         lcd.setCursor(0, 0);
         lcd.print("Program unknown"); 
         delay(5000);       
         emergencystop();
      }   
      drop();  // drop tube 
  }
  else if (evacprogram==0) {

  }  
  else if (evacprogram==20) {
        digitalWrite(airvpin,HIGH);
        pausems(flushlinetime);
        digitalWrite(airvpin,LOW);
        
        digitalWrite(vacvpin,HIGH);
        pausems(flushlinetime);
        digitalWrite(vacvpin,LOW);

        digitalWrite(gasvpin,HIGH);
        pausems(flushlinetime);
        digitalWrite(gasvpin,LOW);  
        pausems(2000);       

  }
  readvacuum();
  printpwminfo();  // show current temperature
  delay(50); 
}

//------------------------------------------------------------------------------------------------
//___________________________SUB-ROUTINES_________________________________________________________
//------------------------------------------------------------------------------------------------
void readvacuum()
{
  tempint=analogRead(thermpin);
  tempfloat=tempint;
  tempfloat=tempfloat/10.0;
  runavgvac=runavgvac*0.9;
  runavgvac=runavgvac+tempfloat;
}

// Convert ADC value to key number

void checkkeys()
{
  if (millis()>timeLastPosition+20){
      newPosition = myEnc.read();
      if (newPosition>oldPosition+1){
          oldPosition = newPosition;
          encoderChanged=1;
       }
       else if (newPosition<oldPosition-1){
           oldPosition = newPosition;
           encoderChanged=-1;
       }
       else {
            encoderChanged=0;    
       }
          
      if (digitalRead(EncoderPress)==0){
          encoderPressed=1;
          delay(200);
      }
      else {
          encoderPressed=0;
      }
   }
   else{
     encoderChanged=0;
     encoderPressed=0;
   } 
}


void printwelcome()
{ 
  if (readinteeprom(eepromisfirstrun)!=firstruncheck){
    lcd.print("FIRSTRUN");  // Print a message to the LCD.
    delay(5000);  
    writeinteeprom(eepromisfirstrun,firstruncheck);
    for (tempint = 0; tempint < amountmenuitems; tempint++) {
      writeinteeprom(firsteepromaddress+tempint*2,defaultvalues[tempint]);
    }
    lcd.clear();
  }
  
  lcd.setCursor(0, 0);
  lcd.print("TR-1200B   ");  // Print a message to the LCD.
  lcd.setCursor(1,0);
  lcd.print("press for setup");
  
  startMillis=millis();
  while (millis() < (startMillis+4000)) {
       checkkeys(); 
       if (encoderPressed >0){ 
          lcd.clear(); 
          lcd.setCursor(0, 0);
          lcd.print("Entering Setup");
          delay(1000);
          setupmenu();
       }
  }
  lcd.clear();
  delay(50); 
}
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

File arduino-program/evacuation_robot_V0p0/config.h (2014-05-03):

//______________________PINS________________________________

const int thermpin =2; // pin for analog-in of supply voltage to thermistor vacuum gauge

const int vacvpin =7;  // pin to MOSFET for vacuum valve
const int airvpin =5; //pin to MOSFET for air vent valve
const int gasvpin =6; // pin to MOSFET for gas valve
const int needlepowerpin =8; //pin to mosfet for needle actuator
const int needlecontrolpin =9; //pin to mosfet for needle actuator

const int rotenpin =13 ; //pin to enable rotator stepper
const int rotdirpin=11 ; //pin to set direction rotator stepper
const int rotsteppin=12 ; //pin to step rotator stepper

const int optopin=10 ; //pin for opto-endstop

const int EncoderA=3;
const int EncoderB=4;
const int EncoderPress=2;

const int lcdsdapin=4; // lcd sda pin (analog 4)
const int lcdsclpin=5; // lcd scl pin (analog 5)

const int rotdrop=11000 ; //steps from center to drop
const int rotshake=5000 ; //steps from center to drop
// (16 microsteps*200=3200steps/rot, gearing is 1/3, so 9600 steps/rot, 2700 steps=105 deg
const int steptimeus=75 ;  //in microseconds: 9600steps/rot, rot in 3 seconds ->3200steps/second -> 1,000,000/3200=313
const int needlemovetime =2500; //time needed for the needle to move (ms)
const int flushlinetime = 1000; //time to flush the lines (vacuum and air open) (ms)
//____________________CONSTANTS__________________________________


const int firstruncheck=346;  //number used for uploading new defaults to eeprom change to replace values staored in eeprom

//________________EEPROM_ADDRESSES_______________________
// all values are stored as integer which need 2 bytes

const int firsteepromaddress=102;
const int eepromisfirstrun=100;

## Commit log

2014-05-03 added 3d printed parts
    3d printed parts for evacuation-robot
    [Belt-protector-spacers.stl, Belt_splitter.stl, Front-plate.stl, Opto-endstop-pcb_mount.stl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]
2014-05-03 added parts
    [Belt_splitter.stl, Evacuation-robot.scad, Pulley_10T-XL.scad, Pulley_13T-XL.scad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]
2014-05-03 added parts and source code
    [Evacuation_robot_arduino_shield.brd, Evacuation_robot_arduino_shield.sch, opto_endstop.brd, opto_endstop.sch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]
2014-06-05 Updated front plate and sled for added rigidity
    more solid design and added adjustability of needle depth
    [Front-plate.stl, Sled.stl]
2014-06-05 Changes to sled and front plate
    More solid design
    [Evacuation-robot.scad]

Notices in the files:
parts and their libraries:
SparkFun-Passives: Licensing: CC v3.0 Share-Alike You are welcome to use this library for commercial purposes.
